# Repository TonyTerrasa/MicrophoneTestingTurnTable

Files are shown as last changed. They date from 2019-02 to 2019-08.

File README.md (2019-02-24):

## Turntable for Gathering Data About MEMS and Other Small Microphones

Designed by Tony Terrasa (Gabriel) under the direct supervision of David Ramsay in the MIT Media Lab. 

## Overview:

This is a physical tool that can be used to test microphones at any and all angles in one plane. It goes in tandem with the Python library included as a submodule for handling audio, collecting data, generating polar patterns for microphones, and interacting with the Arduino and stepper motors required for this build. Data collected with this tool allows one to understand the way a microphone reacts as a function of both angle and frequency, which can have a wide range of applications including but not limited to selective audio capture with microphone arrays. 

## Available Files:

*   STLs - contains STLs of all custom files for this project
*   Drawings - contains technical drawings for this project in both dwg and pdf format
*   SLDWKS - All of the original CAD files for this project
    *   All of these models are entirely parametric and dependent upon a dimensions.txt file. This file will be necessary in order to open and work with the project. 

## Parts:

Many parts for this turntable are of custom geometry and were 3D-printed for which a high-precision Form2 was used. While it is not necessary to 3D print the parts, the parts are designed with tolerances so that axles need to be sanded slightly to create a good push into their target slots. Whatever material they are made out of should be able to bear threads. 

### Purchasable online: 

*   [28BYJ-48 stepper motor](http://eeshop.unl.edu/pdf/Stepper+Driver.pdf)
*   [12-mm diameter slip ring](https://www.adafruit.com/product/1195)
*   [ULN2003 motor driver breakout board](https://www.aliexpress.com/item/5-pcs-ULN2003-Stepper-Motor-Driver-Board-Module/1923223718.html)
*   Male 0.1'' headers
*   9V power supply
*   Pogo pins (pad or through-whole)
*   3M-12 hex screws 
*   3M-30 hex screws
*   3M nuts

### Printables:

*   _Body_ - box-shaped frame onto which the whole system mounts
*   _BoardMount_ - mounting bracket that connects the _MountShaft _and the_ MountBoard_
*   _MountShaft_ - interacts with the _DrivenShaft_ and holds up the microphone boards
*   _DriveShaft_ - solid shaft with a gear, collar, and hole to interface with motor 
*   _DrivenShaft_ - hollow shaft with a gear and collar, driven by the _DriveShaft_
*   _MotorMount_ - mounts the motor to the body 
*   _SlipRingMount_ - mounts the slip ring to the body 

### Boards:

*   _Mount Board_ - PCB which connects the wires from within the table to the _MicBoard_
*   _MicBoard_ - custom PCB for the microphone that is to be tested

## Build 

### Necessary Assembly Tools:

*   Form 2 or other high-precision 3D printer
*   3M tap
*   Various grit sandpaper 
*   Hex screwdriver and small wrench for tightening fasteners

### Build Instructions:

1. Pre set-up
    1. Design, order, and build desired PCBs (see **Boards** sections)
    2. Print all parts and remove support material.
        * When choosing the print orientations, keep in mind that the fit on most of the parts are designed such that sanding will be required to get them to fit snuggly. This was done to allow for supports to be used in the print and sanded back. That being said, avoid supports on areas of the parts that require many precise fits (gears) if possible. 
    3. Solder extensions onto 6 of the wires on the slip ring so that the wires can reach all the way through the _Shaft_ with about 1'' of extra clearance
    4. Tap all appropriate holes. All 2.5mm holes are meant to be tapped for 3M screws. 
2. Insert bearings into their designated holes in the top of the _Body_. The fit should be snug. Sand holes as necessary.
3. Mount Arduino and ULN2003 driver board to _Body _with 3M fasteners.
4. Mount motor and slip ring into _MotorMount_ and _SlipringMount_ respectively. Note that the motor is held to its mount with 2 tapped holes while the slip ring sits freely in its mount.
5. Mount the _MotorMount_ to the floor of the _Body_. The _MotorMount_ goes onto the set of 3 holes. Note that this mount is held to the body via tapped holes that enter through the floor of the body and into the bottom of the mount. 
6. Connect the motor to the output pins on the ULN2003 board, and use jumpers to connect the four input pins on the ULN2003 board with your desired pins on the Arduino. 
7. Insert the _DriveShaft_ and _DrivenShaft_ into their respective bearings. 
    * The _DriveShaft_ goes with the motor. Make sure that the hole at the bottom engages with the shaft of the motor 
    * The _DrivenShaft_ goes with the slip ring. Ensure that the gears mesh appropriately and there are no supports interfering with the rotation all the way around the gears. 
8. Fasten the _MountShaft_ to the _DrivenShaft_ with a 3M screw.
9. Feed the wires from the slip ring up through the _DrivenShaft_ and mount the _SlipringMount_ the the floor of the _Body_. Note this mounting mechanism is the same as for the _MotorMount_.
10. Ensure that all headers and pins are inserted into appropriate headers on _MountBoard_
11. Mount the _MountBoard_ onto the _BoardMount_ and with 3M fasteners around the perimeter.
12. Mount the _MicBoard_ to the _MountBoard_ with the four designated holes, ensuring that appropriate pins and pads align. Note that the pogo pins should push against the screws and the screws should not be tightened too tight as to not break the pogo pins. 

## Boards:

This turntable is designed to allow for the mounting of any microphone that one can create a board for. The boards provided in the CAD are purely for reference for mounting holes for the design of the custom PCBs required for this turntable. The boards already used for data collection with this device were designed by David Ramsay will be posted in the future. See notes below about getting the best sound quality for more information about customizing boards.

The turntable is designed so that the _MountBoard_ stays in place at the top of the _Shaft_ and the _MicBoard_ can be customized for the desired microphone and mounted on top of the _MountBoard_ with spring-loaded pogo pins. The holes for the pogo pins are designed such that through-hole or pad pins can be used.Through-hole pins are used in the CAD. 

## Taking measurements

### Pre set-up

Before starting to take measurements, it is essential that the turntable is fully assembled. The following items will be necessary:

*   Turntable
*   Computer with companion Python library for this project and 2 USB-A ports
*   Audio interface
*   1 speaker
*   XLR cables 
    1. One to connect to the speaker
    2. One customized cable to connect to connect to end via jumpers
*   Lab power supply
*   9V power supply that terminals in female headers
*   USB-A to USB-B cable

### Taking measurement

1. Place the turntable and the speaker on two surfaces at least 6 feet away. It is important to make sure that the middle of the speaker is vertically level with where the microphone sits on the turntable.
2. Connect 9V power supply to the ULN2003 motor driver board. Ensure positive and negative ends are connected correctly. 
3. Connect computer to both the Arduino and audio interface with USB-A to USB-B cables.
4. Connect the microphone to the audio interface with the custom XLR cable, powering and grounding the microphone with the lab power supply. 
5. Connect computer to the audio interface and ensure that both audio can be received from the microphone and outputted to the speakers.
6. See the Python measurement script to ensure that your ports and Arduino are configured correctly. 
7. Run the measurement script.

## **Getting the best sound quality**:

In the first use of this device, several obstacles to good sound quality were encountered. Below is information on such issues and what was done to address them. 

_Grounding_ --  It was important to not ground signal from the microphone to the Arduino. The Arduino ground is not steady enough for high-quality signal reference. A lab power supply was instead used to power the microphone and ground the signal. 

_Amplification_ -- An Op-Amp circuit was incorporated into the _MicBoard_ design to amplify the incoming signal. 

_Balanced Audio_ -- The designed system does not inherently output balanced audio. In an attempt to reduce the noise from the signal, an auxiliary board was used to balance the signal before sending it to the computer.

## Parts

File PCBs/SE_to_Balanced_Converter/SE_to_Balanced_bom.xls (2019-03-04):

Comment | Description | Designator | Footprint | LibRef | Quantity
10uF |  | C1, C5 | 0603C | Capacitor | 2.0
100nF |  | C2, C3, C4, C6 | 0603C | Capacitor | 4.0
Header 2 | Header, 2-Pin | P1, P2 | HDR1X2 | Header 2 | 2.0
Header 4 | Header, 4-Pin | P3 | HDR1X4 | Header 4 | 1.0
Header 3X2 | Header, 3-Pin, Dual row | P4 | HDR2X3 | Header 3X2 | 1.0
1K |  | R1, R2 | 0603R | Resistor | 2.0
1.4k |  | R3 | 0603R | Resistor | 1.0
30k |  | R4 | 0603R | Resistor | 1.0
14k |  | R5 | 0603R | Resistor | 1.0
20k |  | R6 | Pot- TTelec 23 series | Potentiometer | 1.0
AD8476 | Low Power Differential Op-Amp, Single Supply | U1 | RM-8 | AD8476 | 1.0
LME49726 | 2-ch Audio Op Amp, 2.5-5.5V | U2 | MSOP-PowerPad | LME49726 | 1.0

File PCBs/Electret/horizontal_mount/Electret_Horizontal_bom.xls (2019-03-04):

Comment | Description | Designator | Footprint | LibRef | Quantity
1uF |  | C1 | 0603C | Capacitor | 1.0
10nF |  | C2 | 0603C | Capacitor | 1.0
2.2uF |  | C3 | 0603C | Capacitor | 1.0
10uF |  | C5, C6 | 0603C | Capacitor | 2.0
10pF |  | C7 | 0603C | Capacitor | 1.0
100nF |  | C7 | 0603C | Capacitor | 1.0
test point | Connector | J1 | TEST POINT SMD SMALL | CON1 | 1.0
marker | Connector | J4, J5 | TEST POINT SMD SUPER SMALL | CON1 | 2.0
Header 2 | Header, 2-Pin | M1, P1, P2, P3 | HDR1X2 | Header 2 | 4.0
10k |  | R1, R2, Rbias | 0603R | Resistor | 3.0
20k |  | R3 | 0603R | Resistor | 1.0
0 |  | R4 | 0603R | Resistor | 1.0
100k |  | R5 | 0603R | Resistor | 1.0
50 |  | R6 | 0603R | Resistor | 1.0
TPS73533 | TPS 500mA LDO, 3.3V | U2 | SON_6LEAD_TI_TPS | TPS73533 | 1.0
OPA2364 | TI 1.8-5V Op Amp, 7MHz GBW | U3 | SOIC8 | OPA2364 | 1.0

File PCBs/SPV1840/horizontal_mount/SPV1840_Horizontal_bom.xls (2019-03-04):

Comment | Description | Designator | Footprint | LibRef | Quantity
1uF |  | C1 | 0603C | Capacitor | 1.0
10nF |  | C2 | 0603C | Capacitor | 1.0
2.2uF |  | C3 | 0603C | Capacitor | 1.0
100nF |  | C4, C7 | 0603C | Capacitor | 2.0
10uF |  | C5, C6 | 0603C | Capacitor | 2.0
test point | Connector | J1 | TEST POINT SMD SMALL | CON1 | 1.0
marker | Connector | J4, J5 | TEST POINT SMD SUPER SMALL | CON1 | 2.0
Header 2 | Header, 2-Pin | P1, P2, P3 | HDR1X2 | Header 2 | 3.0
10k |  | R1, R2 | 0603R | Resistor | 2.0
20k |  | R3 | 0603R | Resistor | 1.0
2k |  | R4 | 0603R | Resistor | 1.0
SPV1840LR5H-B | Knowles SPV1840LR5H-B Analog Bottom Port MEMS Mic | U1 | SPV1840LR5H-B | SPV1840LR5H-B | 1.0
TPS73533 | TPS 500mA LDO, 3.3V | U2 | SON_6LEAD_TI_TPS | TPS73533 | 1.0
OPA2364 | TI 1.8-5V Op Amp, 7MHz GBW | U3 | SOIC8 | OPA2364 | 1.0

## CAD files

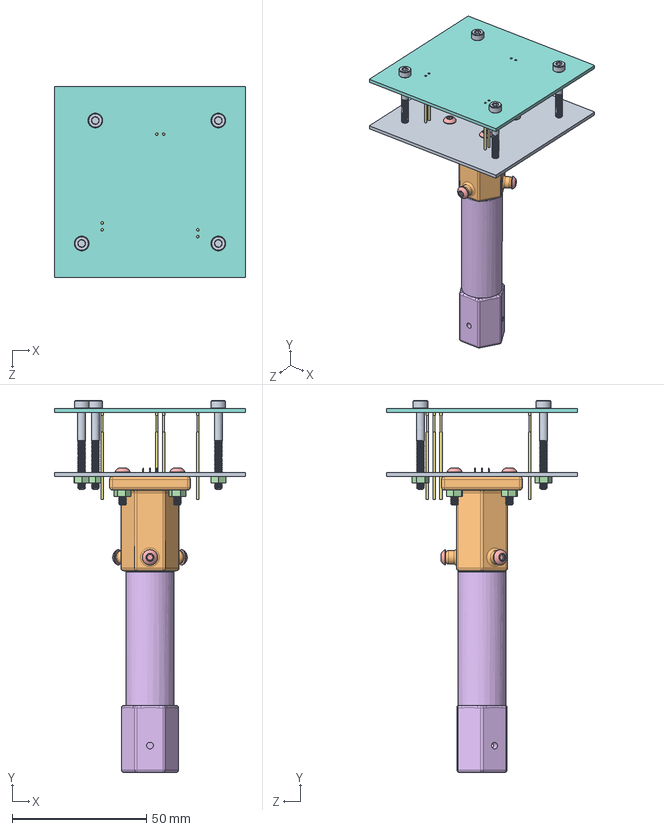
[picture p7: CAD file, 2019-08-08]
SLDWKS/TT_MicMount.SLDASM
71.1 x 138.3 x 71.1 mm
TT_MountBoard
TT_BoardMount
FemaleHeader-2 x 3
HexNut-M3 x 9
Screw-M3-12 x 7
TT_MountShaft
PogoPin-33 x 7
TT_MicBoard
Screw-M3-30 x 5

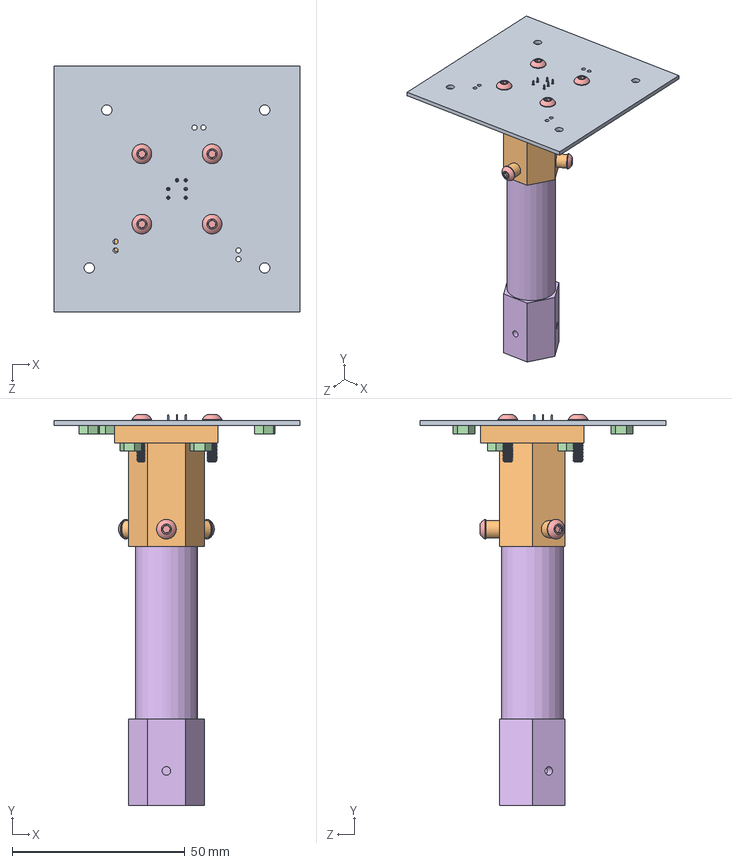
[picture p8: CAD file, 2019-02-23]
SLDWKS/MicMount - Copy.SLDASM
71.1 x 113.2 x 71.1 mm
MountBoard
BoardMount
FemaleHeader x 3
Nut x 8
Screw x 7
Shaft_2

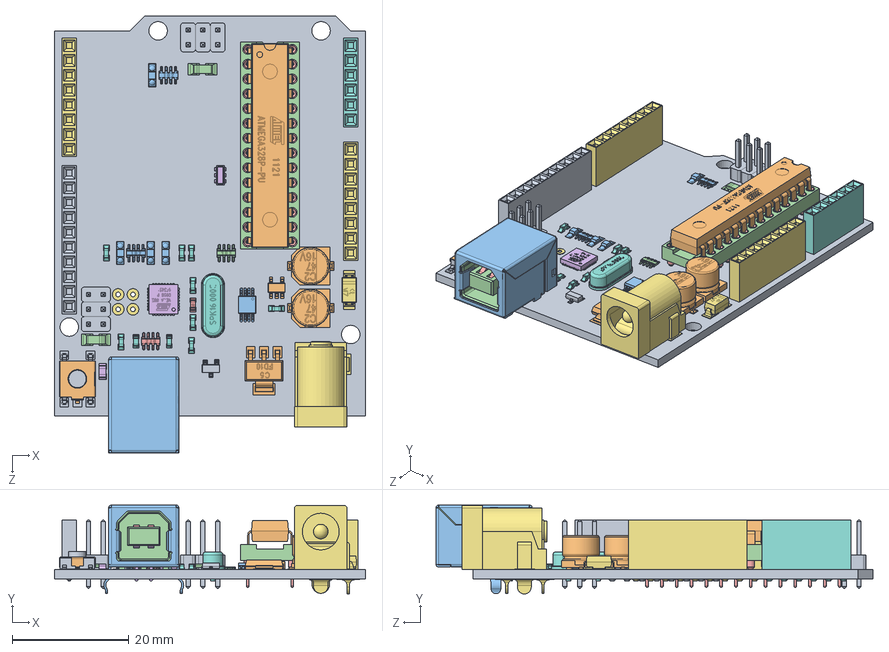
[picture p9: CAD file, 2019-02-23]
SLDWKS/UNO/UNO.SLDASM
53.3 x 15.2 x 74.9 mm
unoboard blue
47uf CAP Dcase x 2
USB SHELL
USB core
usb top contact x 2
usb btm contact x 2
power jack
crystal
2pin_header__02 x 6
nano - reg
led x 4
dip28
dip socket pin x 28
atmega16u2
8 PORT HEADER x 2
6 PORT HEADER
10 PORT HEADER
ATMEL328P
102 RESISTOR PACK x 2
103 RESISTOR PACK
220 RESISTOR PACK
16mhz crystal - measured
PADS001
603 cap on pad x 8
ssot3
lmv358
lp2985dgkr
cd1206 diode x 2
603 resistor
blm21
m7 diode
MLC0603 x 2
RESET CORE
RESET

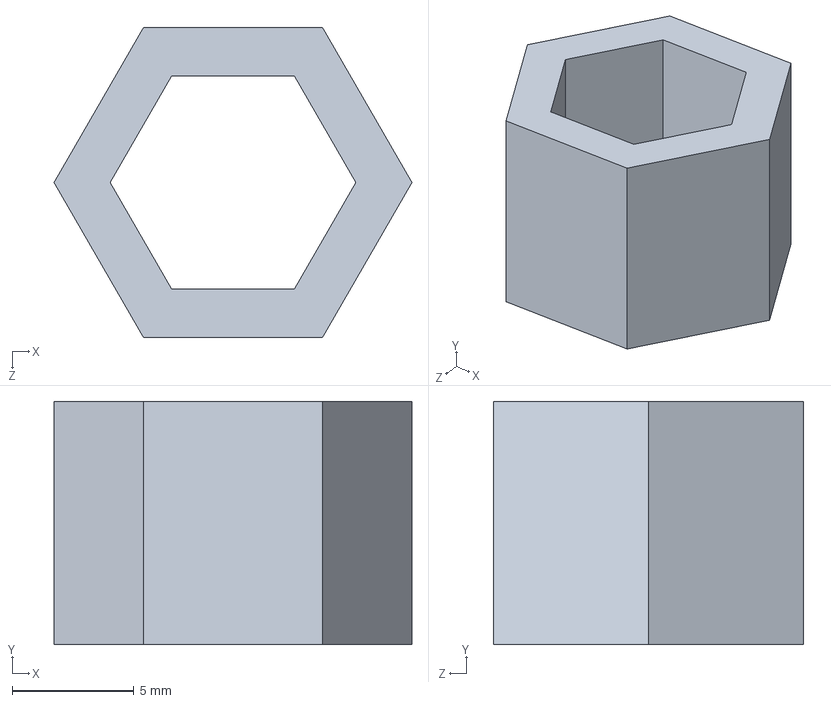
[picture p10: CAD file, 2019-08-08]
STLs/tests/shaftDimTest.SLDPRT
14.7 x 10.0 x 12.8 mm

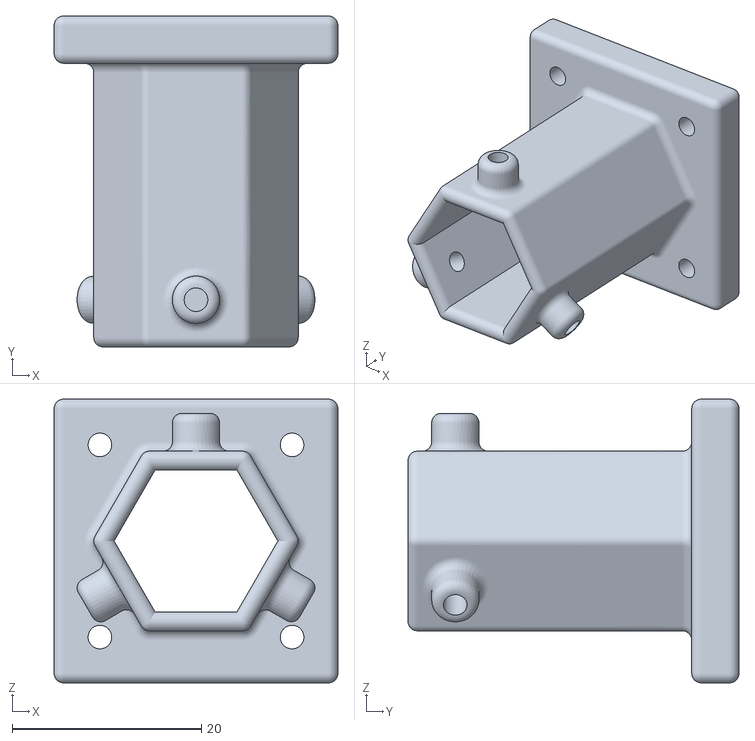
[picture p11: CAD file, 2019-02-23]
STLs/TT_BoardMount.STL
30.0 x 35.0 x 30.0

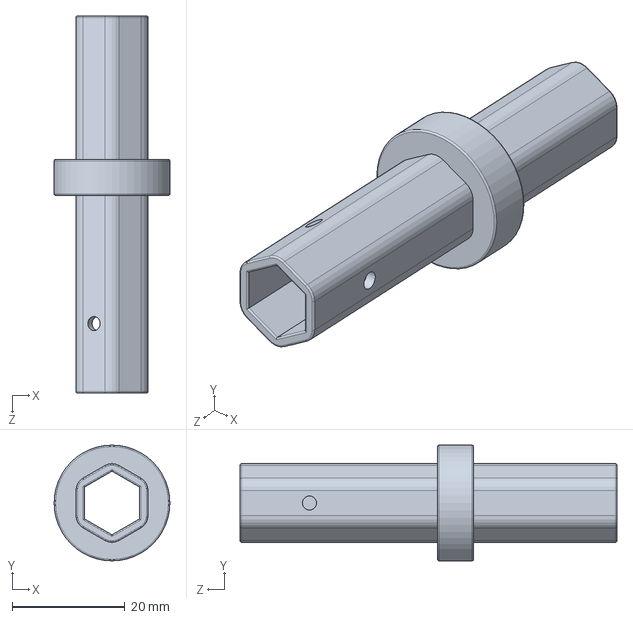
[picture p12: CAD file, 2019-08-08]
SLDWKS/TT_DrivenShaft.SLDPRT
20.5 x 20.5 x 66.8 mm

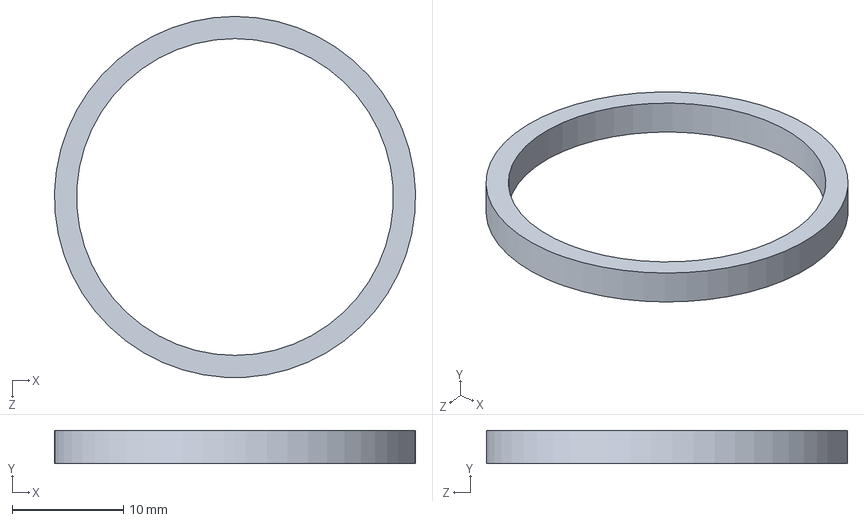
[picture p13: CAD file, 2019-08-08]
STLs/tests/bearingtest.SLDPRT
32.5 x 3.00 x 32.5 mm

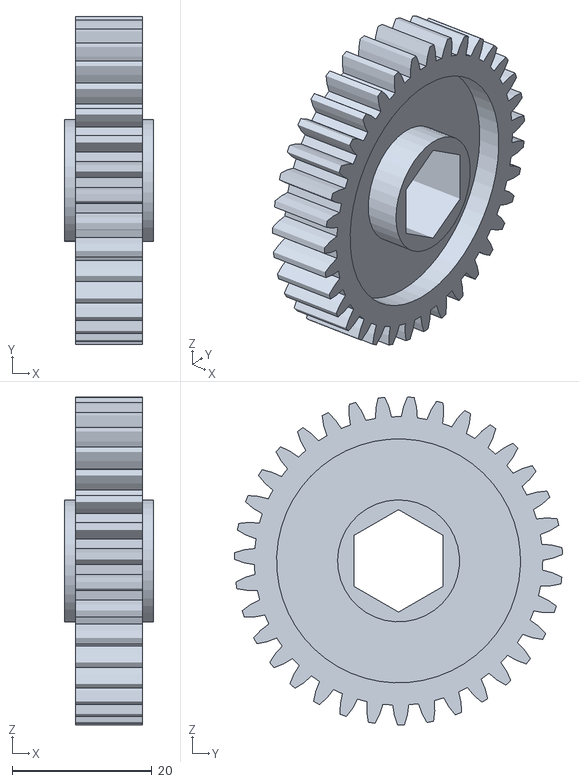
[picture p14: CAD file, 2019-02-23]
STLs/TT_DrivenShaft-Assm - HexGear-35T-1.75-1.STL
12.7 x 47.0 x 47.0

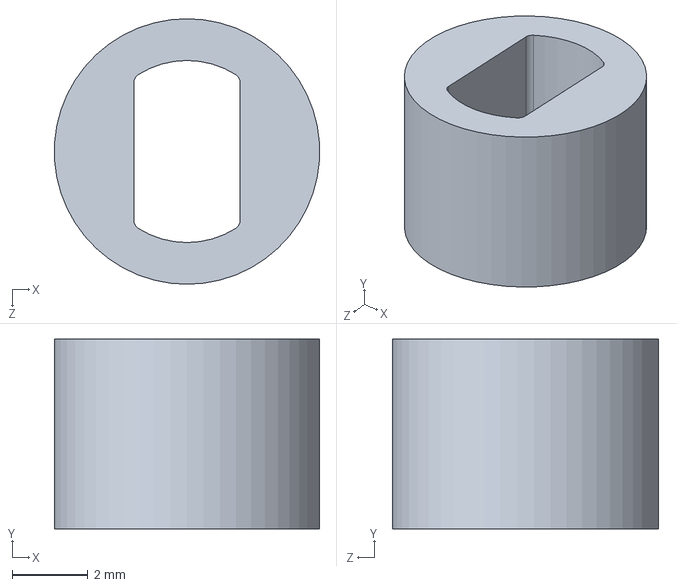
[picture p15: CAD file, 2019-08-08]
STLs/tests/MotHoleTest.SLDPRT
6.99 x 5.00 x 7.00 mm

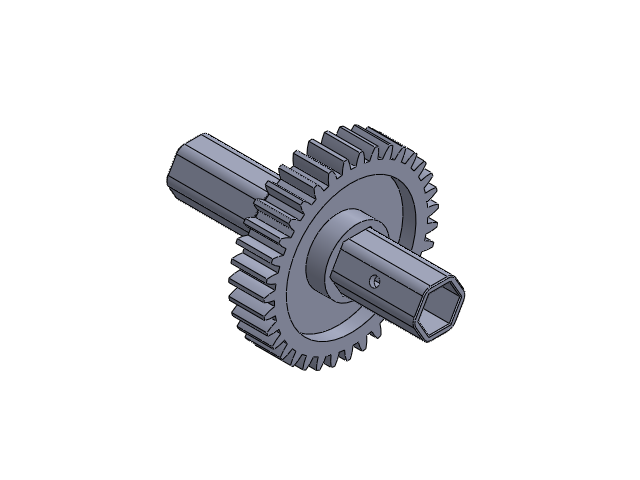
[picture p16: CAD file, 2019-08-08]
SLDWKS/TT_DrivenShaft-Assm.SLDASM
TT_DrivenShaft
HexGear-35T-1.75

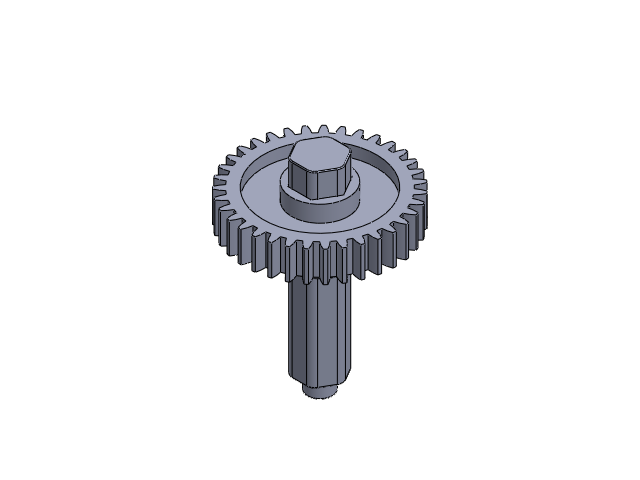
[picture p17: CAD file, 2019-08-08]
SLDWKS/TT_DriveShaft-Assm.SLDASM
TT_DriveShaft
HexGear-35T-1.75

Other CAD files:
SLDWKS/UNO/USB type b.SLDPRT.sldasm
SLDWKS/UNO/dip28.sldasm
SLDWKS/UNO/RESET BUTTON.sldasm
SLDWKS/UNO/10 PORT HEADER.sldprt
SLDWKS/UNO/RESET.sldprt
SLDWKS/UNO/unoboard blue.sldprt
STLs/TT_DriveShaft-Assm - HexGear-35T-1.75-1.STL
Drawings/BoardMount.SLDDRW
Drawings/Body.SLDDRW
Drawings/DriveShaft.SLDDRW
Drawings/DrivenShaft.SLDDRW
Drawings/MicBoard.SLDDRW
Drawings/MotorMount.SLDDRW
Drawings/MountBoard.SLDDRW
Drawings/SlipRingMount.SLDDRW
SLDWKS/FemaleHeader-2.SLDPRT
SLDWKS/HexBearing-0.5in.SLDPRT
SLDWKS/HexGear-35T-1.75.SLDPRT
SLDWKS/HexNut-M3.SLDPRT
SLDWKS/PogoPin-33.SLDPRT
SLDWKS/Screw-M3-12.SLDPRT
SLDWKS/Screw-M3-30.SLDPRT
SLDWKS/SlipRing-12-12wire.SLDPRT
SLDWKS/StepperDriver-ULN2003.SLDPRT
SLDWKS/StepperMotor-28BYJ48.SLDPRT
SLDWKS/TT_BoardMount.SLDPRT
SLDWKS/TT_Body.SLDPRT
SLDWKS/TT_DriveShaft.SLDPRT
SLDWKS/TT_DriveShaft_merge.SLDPRT
SLDWKS/TT_MicBoard.SLDPRT
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

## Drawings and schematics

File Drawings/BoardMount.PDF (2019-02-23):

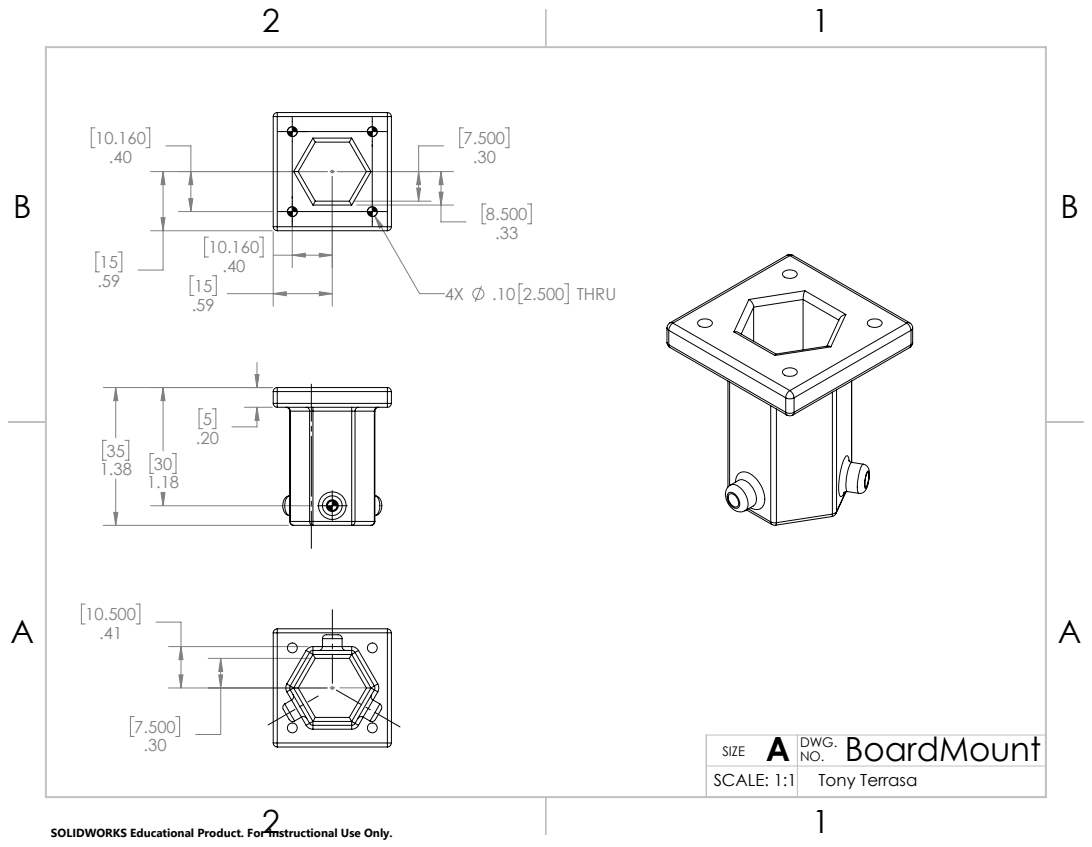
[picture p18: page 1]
.10 2.500 THRU

BoardMount DWG. A NO. SIZE

SCALE: 1:1 | Tony Terrasa

SOLIDWORKS Educational Product. For Instructional Use Only.

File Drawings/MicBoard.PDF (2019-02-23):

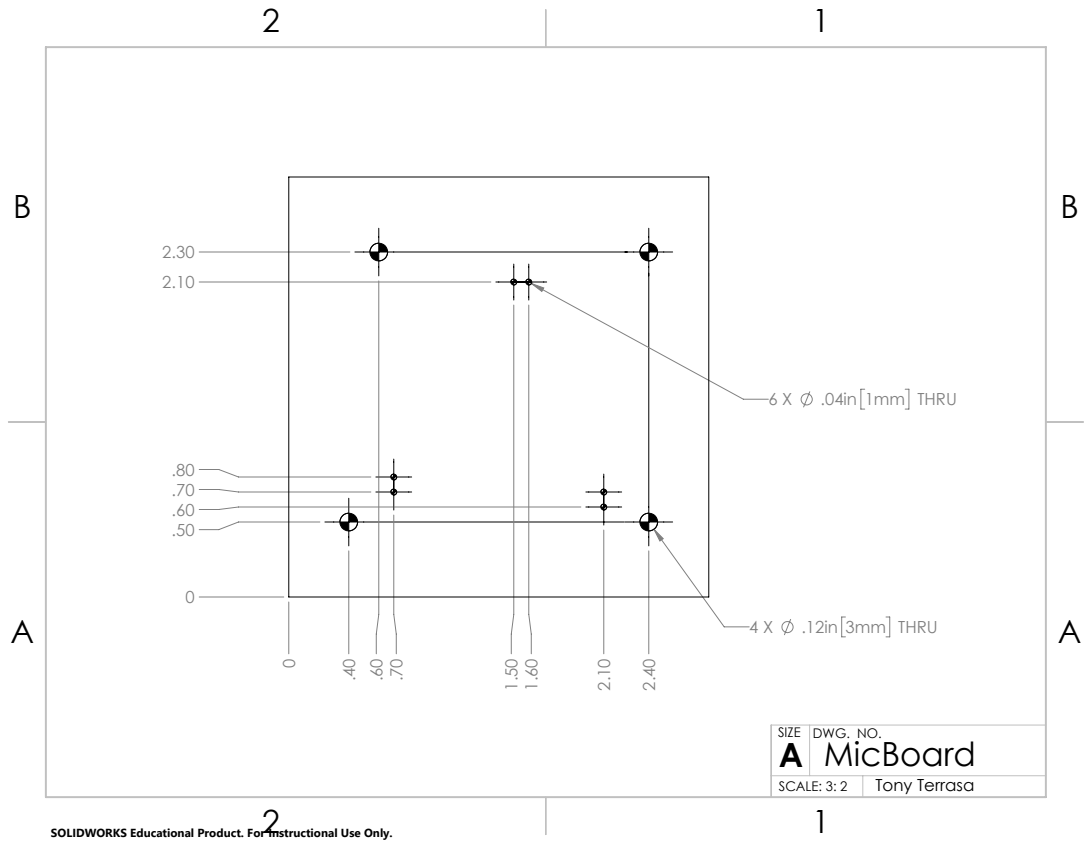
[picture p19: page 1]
.12in 3mm THRU; .04in 1mm THRU

SIZE A | DWG. NO. MicBoard

SCALE: 3: 2 | Tony Terrasa

SOLIDWORKS Educational Product. For Instructional Use Only.

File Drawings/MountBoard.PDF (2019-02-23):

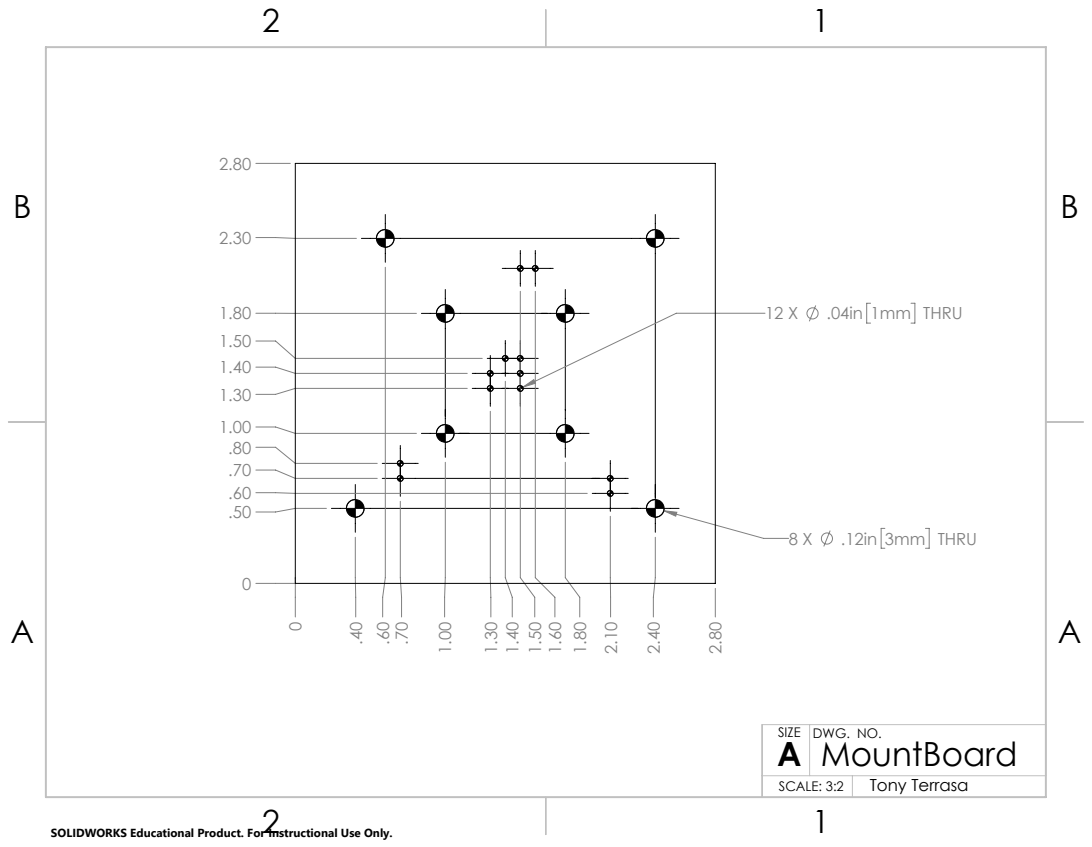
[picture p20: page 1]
.12in 3mm THRU; .04in 1mm THRU

SIZE A | DWG. NO. MountBoard

SCALE: 3:2 | Tony Terrasa

SOLIDWORKS Educational Product. For Instructional Use Only.

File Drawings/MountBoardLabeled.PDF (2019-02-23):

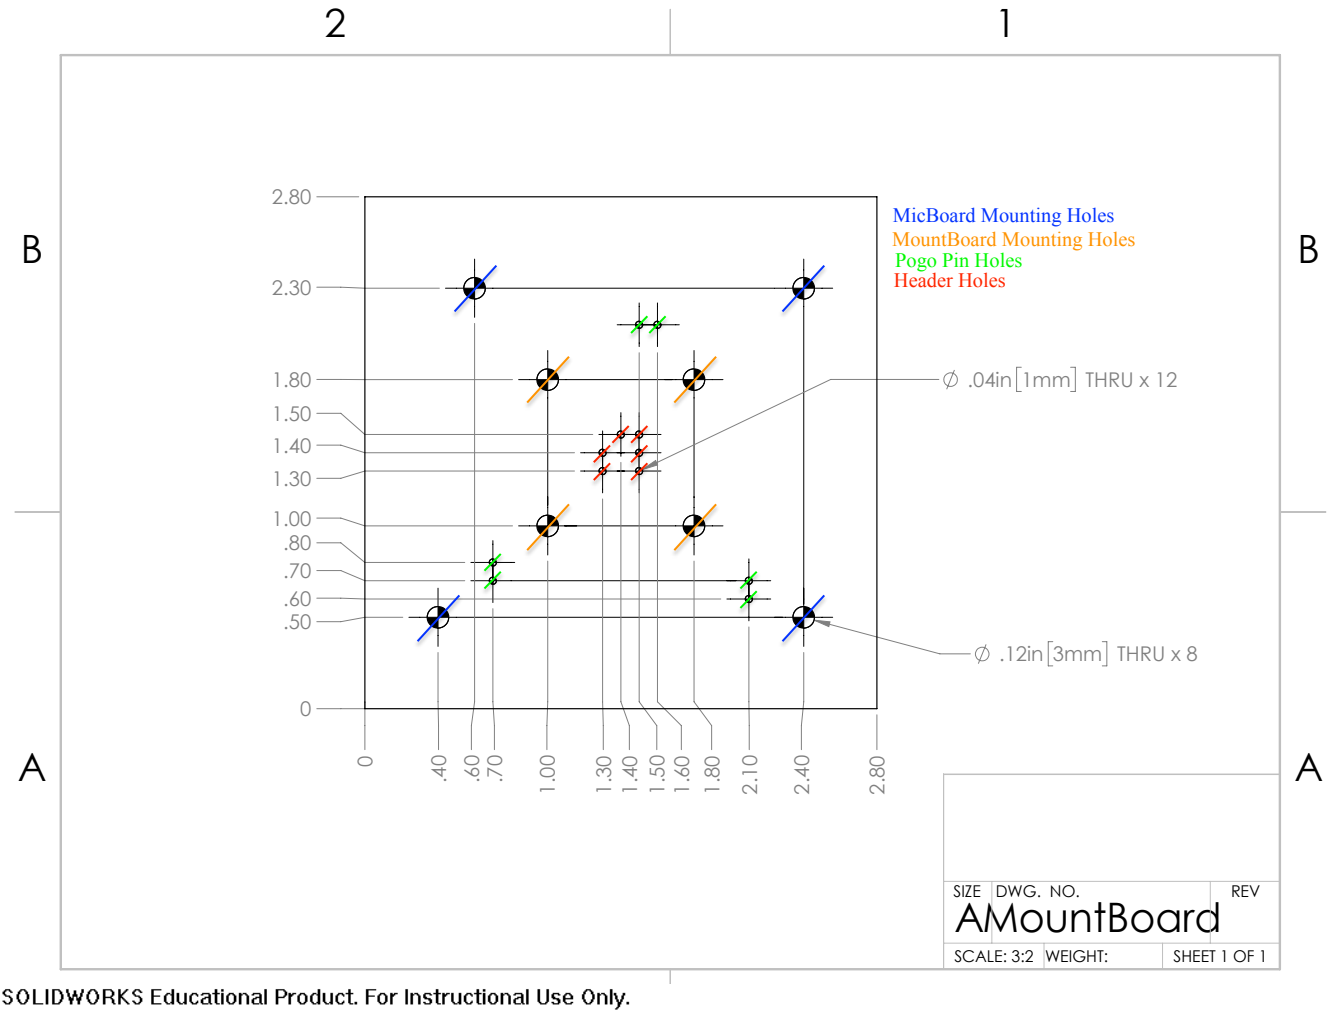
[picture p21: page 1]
.12in 3mm THRU x 8; .04in 1mm THRU x 12

SIZE A MountBoard | DWG. NO. | REV

SCALE: 3:2 | WEIGHT: | SHEET 1 OF 1

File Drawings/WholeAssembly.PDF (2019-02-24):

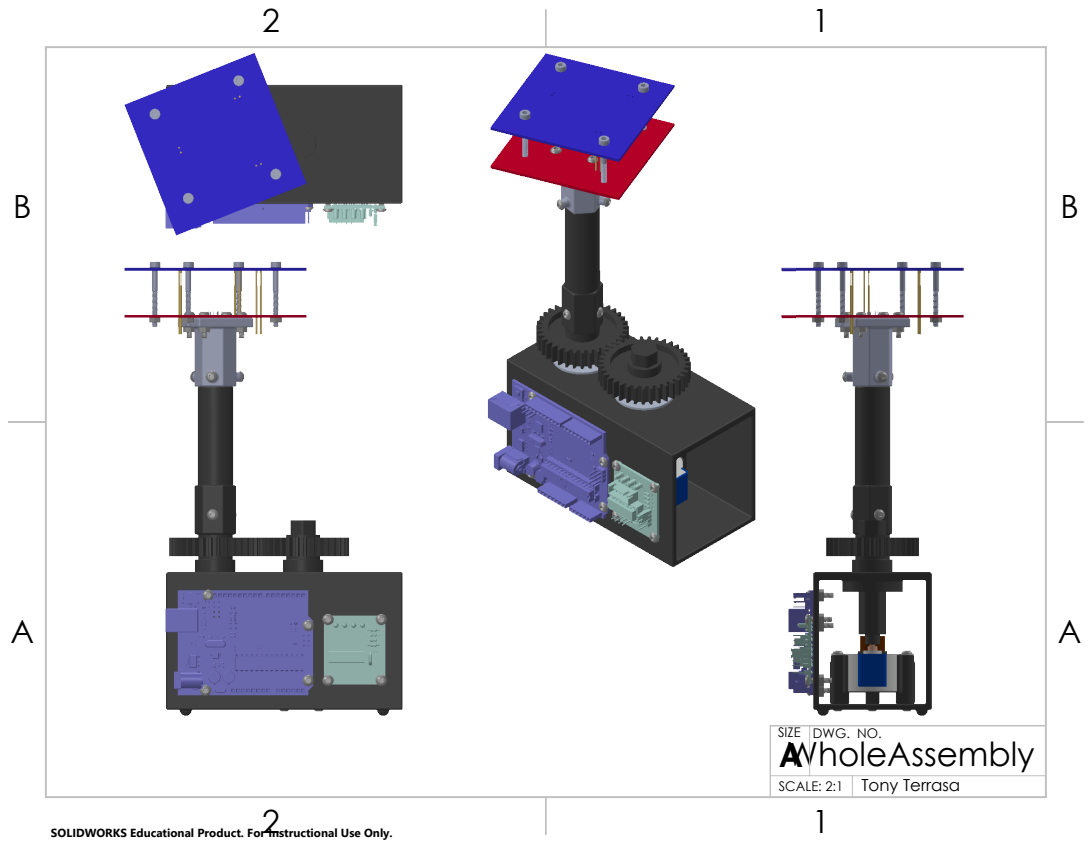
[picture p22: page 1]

SIZE A WholeAssembly | DWG. NO.

SCALE: 2:1 | Tony Terrasa

SOLIDWORKS Educational Product. For Instructional Use Only.

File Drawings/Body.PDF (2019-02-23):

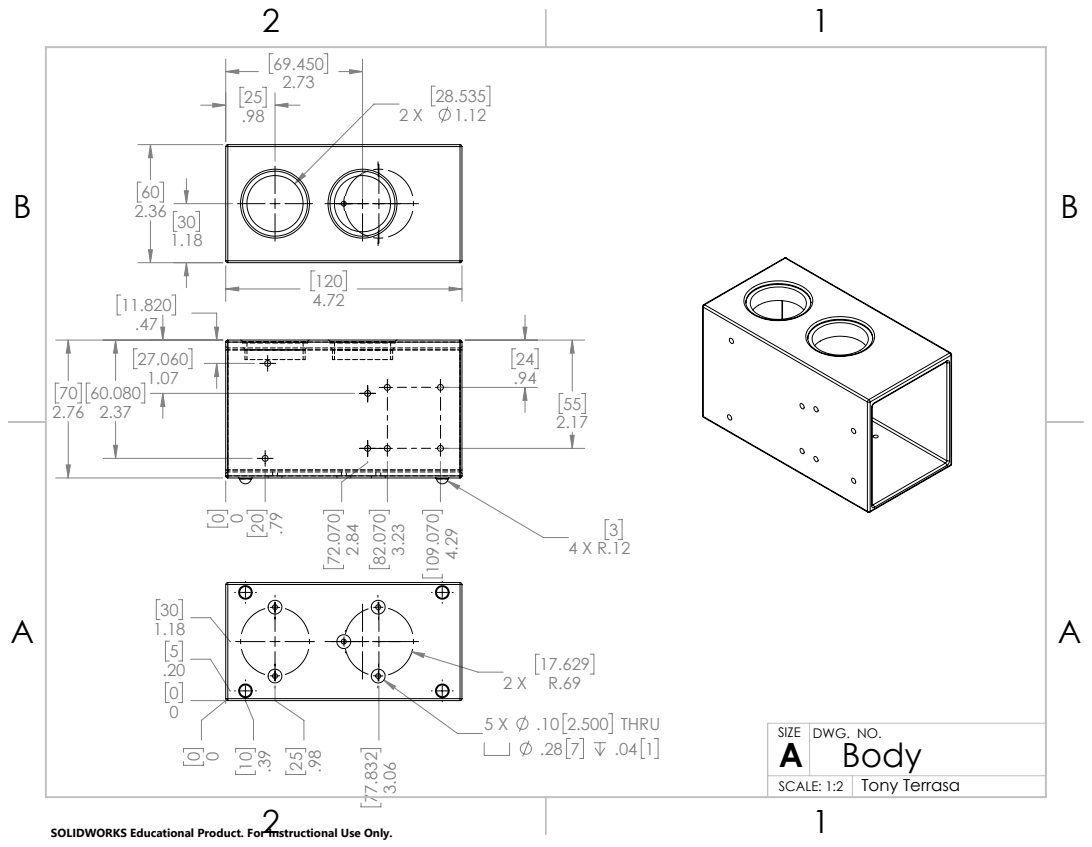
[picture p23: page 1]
.10 2.500 THRU

SIZE A | DWG. NO. Body

SCALE: 1:2 | Tony Terrasa

SOLIDWORKS Educational Product. For Instructional Use Only.

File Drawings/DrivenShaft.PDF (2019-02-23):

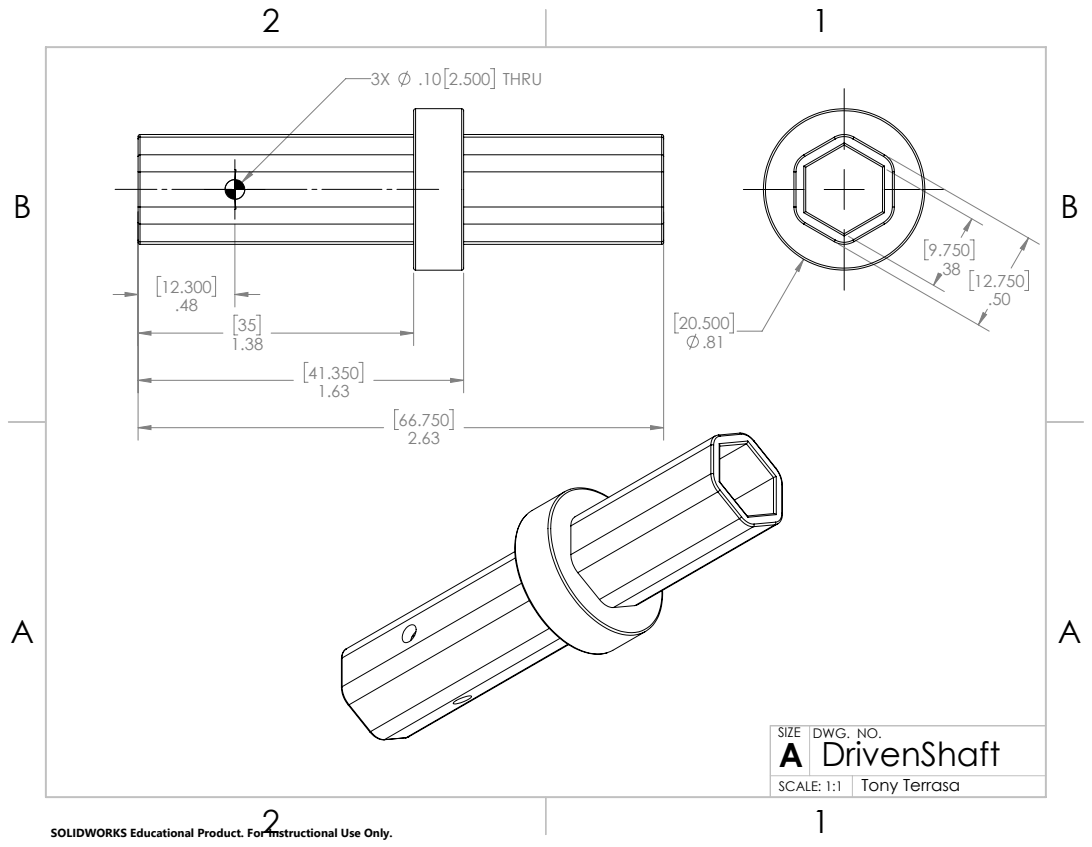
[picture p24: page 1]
.10 2.500 THRU

SIZE A | DWG. NO. DrivenShaft

SCALE: 1:1 | Tony Terrasa

SOLIDWORKS Educational Product. For Instructional Use Only.

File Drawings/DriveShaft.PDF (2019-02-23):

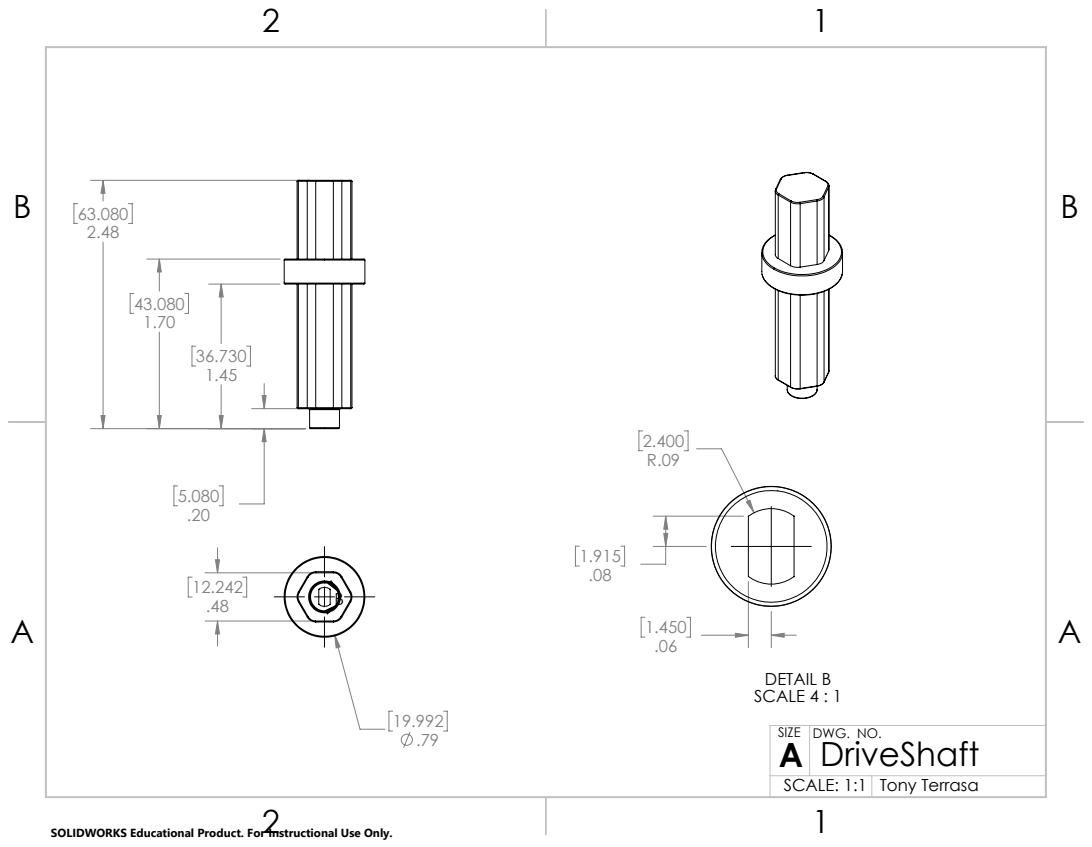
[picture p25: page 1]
DETAIL B SCALE 4 : 1

SIZE A | DWG. NO. DriveShaft

SCALE: 1:1 | Tony Terrasa

SOLIDWORKS Educational Product. For Instructional Use Only.

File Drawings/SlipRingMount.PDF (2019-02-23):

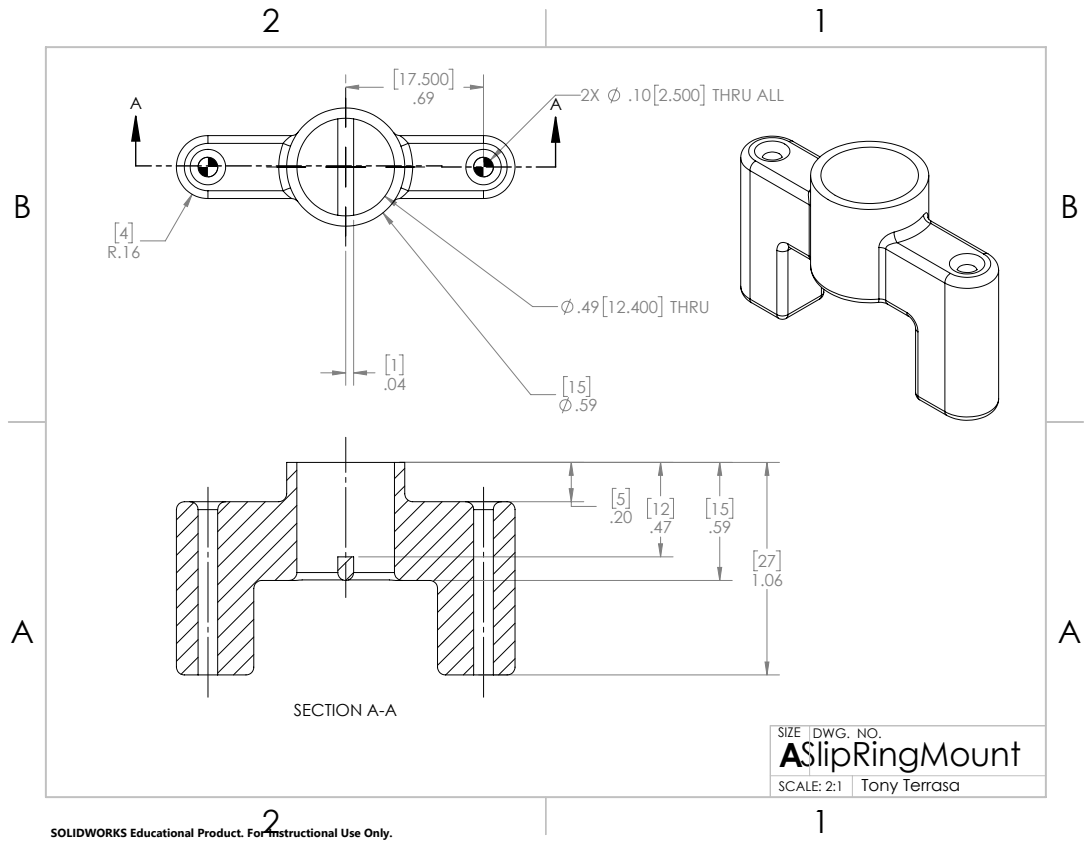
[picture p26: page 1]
.10 2.500 THRU ALL; .49 12.400 THRU; SECTION A-A

SIZE A SlipRingMount | DWG. NO.

SCALE: 2:1 | Tony Terrasa

SOLIDWORKS Educational Product. For Instructional Use Only.

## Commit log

2019-02-23 fist commit
    [10 PORT HEADER.sldprt, 102 RESISTOR PACK.sldprt, 103 RESISTOR PACK.sldprt, 16mhz crystal - measured.sldprt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]
2019-02-24 add whole assembly pdf
    [TT_BoardMount.SLDPRT, TT_Body.SLDPRT, TT_DriveShaft-Assm.SLDASM, TT_DriveShaft.SLDPRT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]
2019-03-04 PCB schematics, BOMs, links to osh park ordering
    [Electret_Horizontal_bom.xls, Electret_Vertical_bom.xls, SE_to_Balanced_bom.xls, SPV1840_Horizontal_bom.xls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]
2019-03-04 naming files
    [SPW2430_Horizontal_bom.xls, SPW2430_Vertical_bom.xls]
2019-08-08 DB add
    [MotHoleTest.SLDPRT, MotHoleTest.STL, TT_BoardMount.SLDPRT, TT_Body.SLDPRT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]
